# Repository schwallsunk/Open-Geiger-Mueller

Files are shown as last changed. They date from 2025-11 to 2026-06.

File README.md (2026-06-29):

# Open Geiger Müller Counter

This repository should provide all the needed parts for the construction of low-cost entry-level Geiger Müller (GM) counter system. This counter was build by request from the students of 151-0163-00L  Nuclear Energy Conversion at ETH Zürich. For a more complete description of the project please read the [manual](https://github.com/schwallsunk/Open-Geiger-Mueller/blob/main/Geiger_counter_manual_final.pdf).

The repository itself is subdivided into two two main parts. The hardware parts contains all the relevant EDA files created in KiCAD v9. The software directory contains all the different code written and tested for and on the hardware.

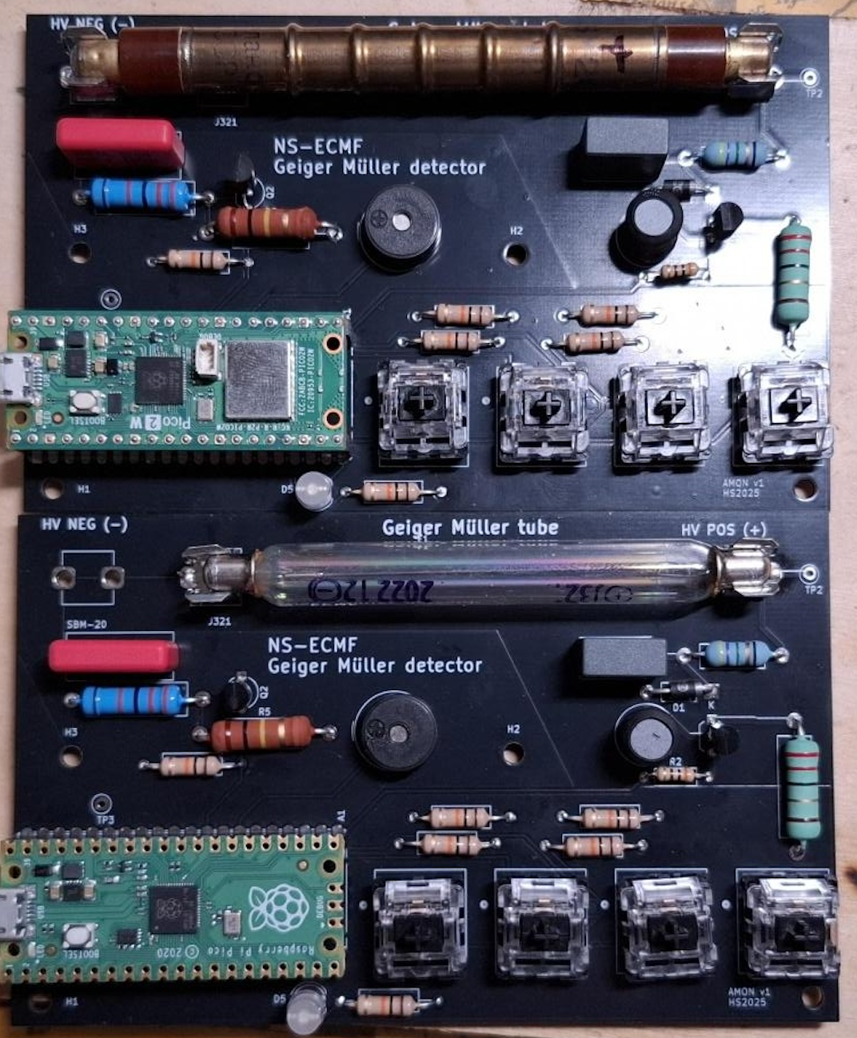
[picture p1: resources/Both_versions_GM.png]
Both GM-counters completed with J321 GM-tube as well as SBM-20 tube


## The Geiger Müller chamber :radioactive:
The detector is based on either the chinese J321 GM-tube or the soviet SBM-20 GM-tube (can be varied by soldering the negative receptacle either into the spot closer or further away from the HV terminal). The J321 can be easily bought through Aliexpress or ebay whereas for the SBM-20 tube you need to revert to ebay only. 
Due to the overall bigger detection volume of the SBM-20 tube compared with the J321 tube, the sensitivity of the soviet tube will be much higher at the cost of roughly double the price of the J321 tube.

## Microcontroller
The microcontroller of choice here is the Rasperry Pico 2W (rp2350 + wifi chipset), allowing for programming in a multitude of languages (Micropython, Arduino, C++, C), lowering the overall barrier to entry into microcontroller (uC) programming. But the PCB itself also supports the Pico W or any other uC with a fitting pin out. 
The W version of the uC also offers a wireless chip set which supports WiFi as well as Bluetooth connectivity, for which a micropython example is available. This example sends the activity according to the Bluetooth LE standard wirelessly to a receiving device. 
But in case of budgetary concerns, a Rasperry Pico can also be used as a drop-in replacement. The RISC-V-based implementation in this repository might then not work, though.

### Without IDE install
For an easier starting point, there is a precompiled firmware already available in this repository under [FW-file](https://github.com/schwallsunk/Open-Geiger-Mueller/blob/main/software/cpp/Counter_cpp_RISC-V.uf2). This file can be easily flashed by holding down the only button on the Raspberry Pico and plugging it into the USB port of the PC. 
The Pico will then appear as a mass storage device (The button on the Pico can be released at this point ) onto which the given firmware .uf2 file can be dragged and dropped onto it. The microcontroller will reboot by itself as soon as the new firmware file is fully transferred.
From there on, the clicking noise of the background radiation should be heard.

### IDE firmware development
If the goal is to do micropython code development, the following documentation [chapter 4](https://datasheets.raspberrypi.com/pico/raspberry-pi-pico-python-sdk.pdf) might be useful. All the given Micropython examples can be copied and pasted into the IDE and directly deployed. 
For the C/C++ code part, there is either a way to do full code development with the [C/C++ IDE](https://pip-assets.raspberrypi.com/categories/610-raspberry-pi-pico/documents/RP-008276-DS-1-getting-started-with-pico.pdf?disposition=inline), where the given code example can be copied and pasted into the given editor and then, at a later stag,e converted into a binary.  

## Electronics

### Parts sourcing
The sourcing of the components for this project was done entirely through the [LCSC](https://www.lcsc.com/) except for the GM-tube as well as the Raspberry Pico 2W. The GM-tube was bought off [EBAY SBM-20 search](https://www.ebay.com/sch/i.html?_nkw=sbm20&_sacat=0&_from=R40&_trksid=p4624852.m570.l1313) and the Pico 2W can be bought from your local electronics reseller.

### PCB manufacturing
The custom printed circuit board (PCB) itself was produced by sending the relevant gerber files to [JLCPCB](https://www.jlcpcb.com/) and choosing a black finish apart from that there is nothing special to consider when ordering them. The relevant gerber files are all merged into a single zip. This zip can be found in the hardware part of this repository.

### BOM 
| LCSC part number | Part description                                          | Amount | Price per piece (USD/piece) | Label of Part on PCB                    |
|------------------|-----------------------------------------------------------|--------|-----------------------------|----------------------------------------|
| C252915          | 2.048kHz 3.3V Electromagnetic Through Hole Buzzer         | 1      | 0.1854                      | BZ1                                    |
| C49234238        | Through Hole Pushbutton Switches RoHS                     | 4      | 0.0809                      | SW1, SW2, SW3, SW4                     |
| C2894588         | Carbon Film Resistor 300Ω                                 | 1      | 0.0043                      | R2                                     |
| C122827          | Metal Film Resistor 22Ω 3W                                | 1      | 0.0392                      | R1                                     |
| C2686215         | 10nF -40°C~+110°C ±5% 1kV)                                | 1      | 0.0969                      | C1                                     |
| C714352          | Carbon Film Resistor 10kΩ 500mW                           | 6      | 0.0081                      | R6,R8,R10,R11,R12,R13                  |
| C142864          | Cylindrical Clip Through Hole,P=7.6mm Fuseholders RoHS    | 2      | 0.1619                      | HV POS (+) and either J321 or SBM-20   |
| C20613339        | 20mA 5 mm flat-head LED                                   | 1      | 0.1041                      | D5                                     |
| C433559          | Metal Film Resistor 22kΩ 3W                               | 1      | 0.0549                      | R4                                     |
| C5156722         | 40V 625mW 200mA NPN TO-92 Single Bipolar Transistors RoHS | 1      | 0.0391                      | Q2                                     |
| C30190409        | Glass Glaze Resistor 4.7MΩ                                | 1      | 0.0553                      | R3                                     |
| C2924242         | 100mA 10mH ±10% Drum-core inductor                        | 1      | 0.173                       | L1                                     |
| C152300          | 30A 175ns 600V 1V@1A 1A DO-41 Single Diodes RoHS          | 1      | 0.0655                      | D1 => look at polarity when installing |
| C256388          | 400V 2.1W 1.5A NPN TO-92 Single Bipolar Transistors RoHS  | 1      | 0.1451                      | Q1                                     |
| C122214          | 100kΩ 1W ±250ppm/°C                                       | 1      | 0.0923                      | R5                                     |
| C7499336         | Pin header 2.54mm 20P                                     | 2      | 0.1601                      | A1 both rows                           |
| C434407          | 220pF capacitor                                           | 1      | 0.2914                      | C2                                     |

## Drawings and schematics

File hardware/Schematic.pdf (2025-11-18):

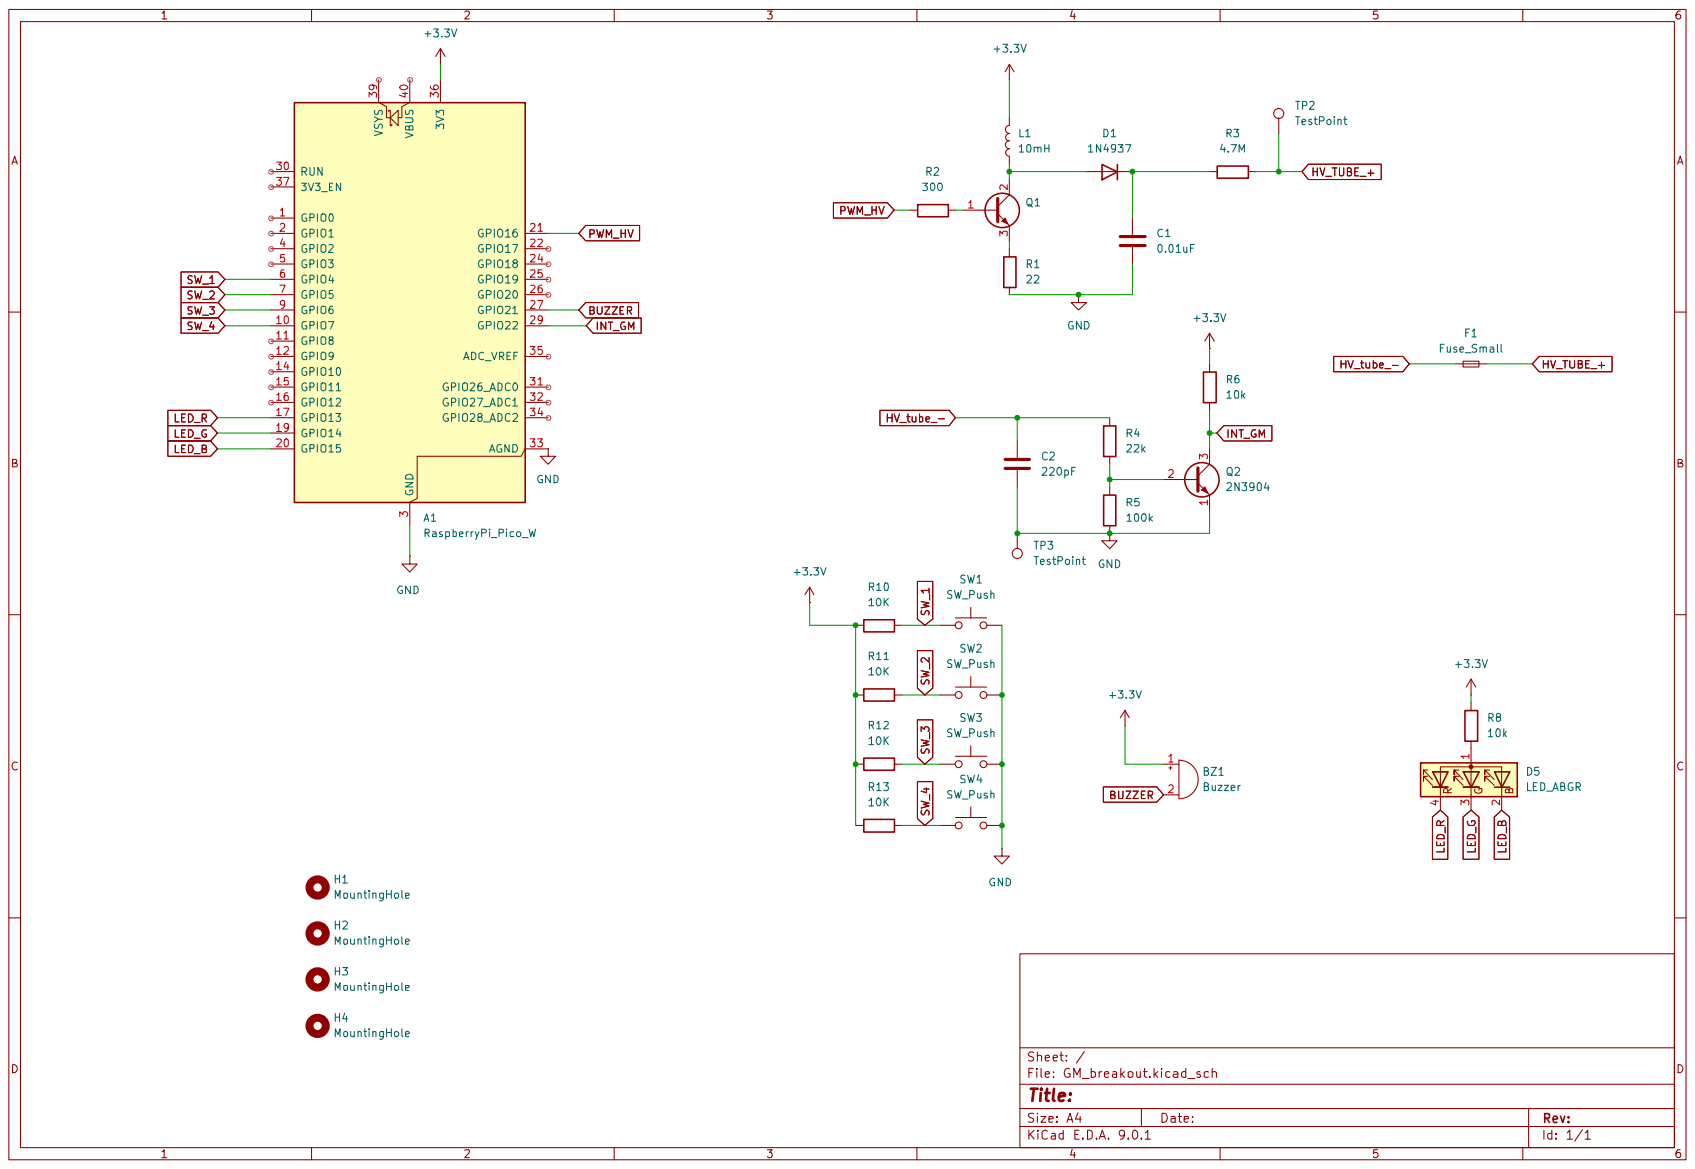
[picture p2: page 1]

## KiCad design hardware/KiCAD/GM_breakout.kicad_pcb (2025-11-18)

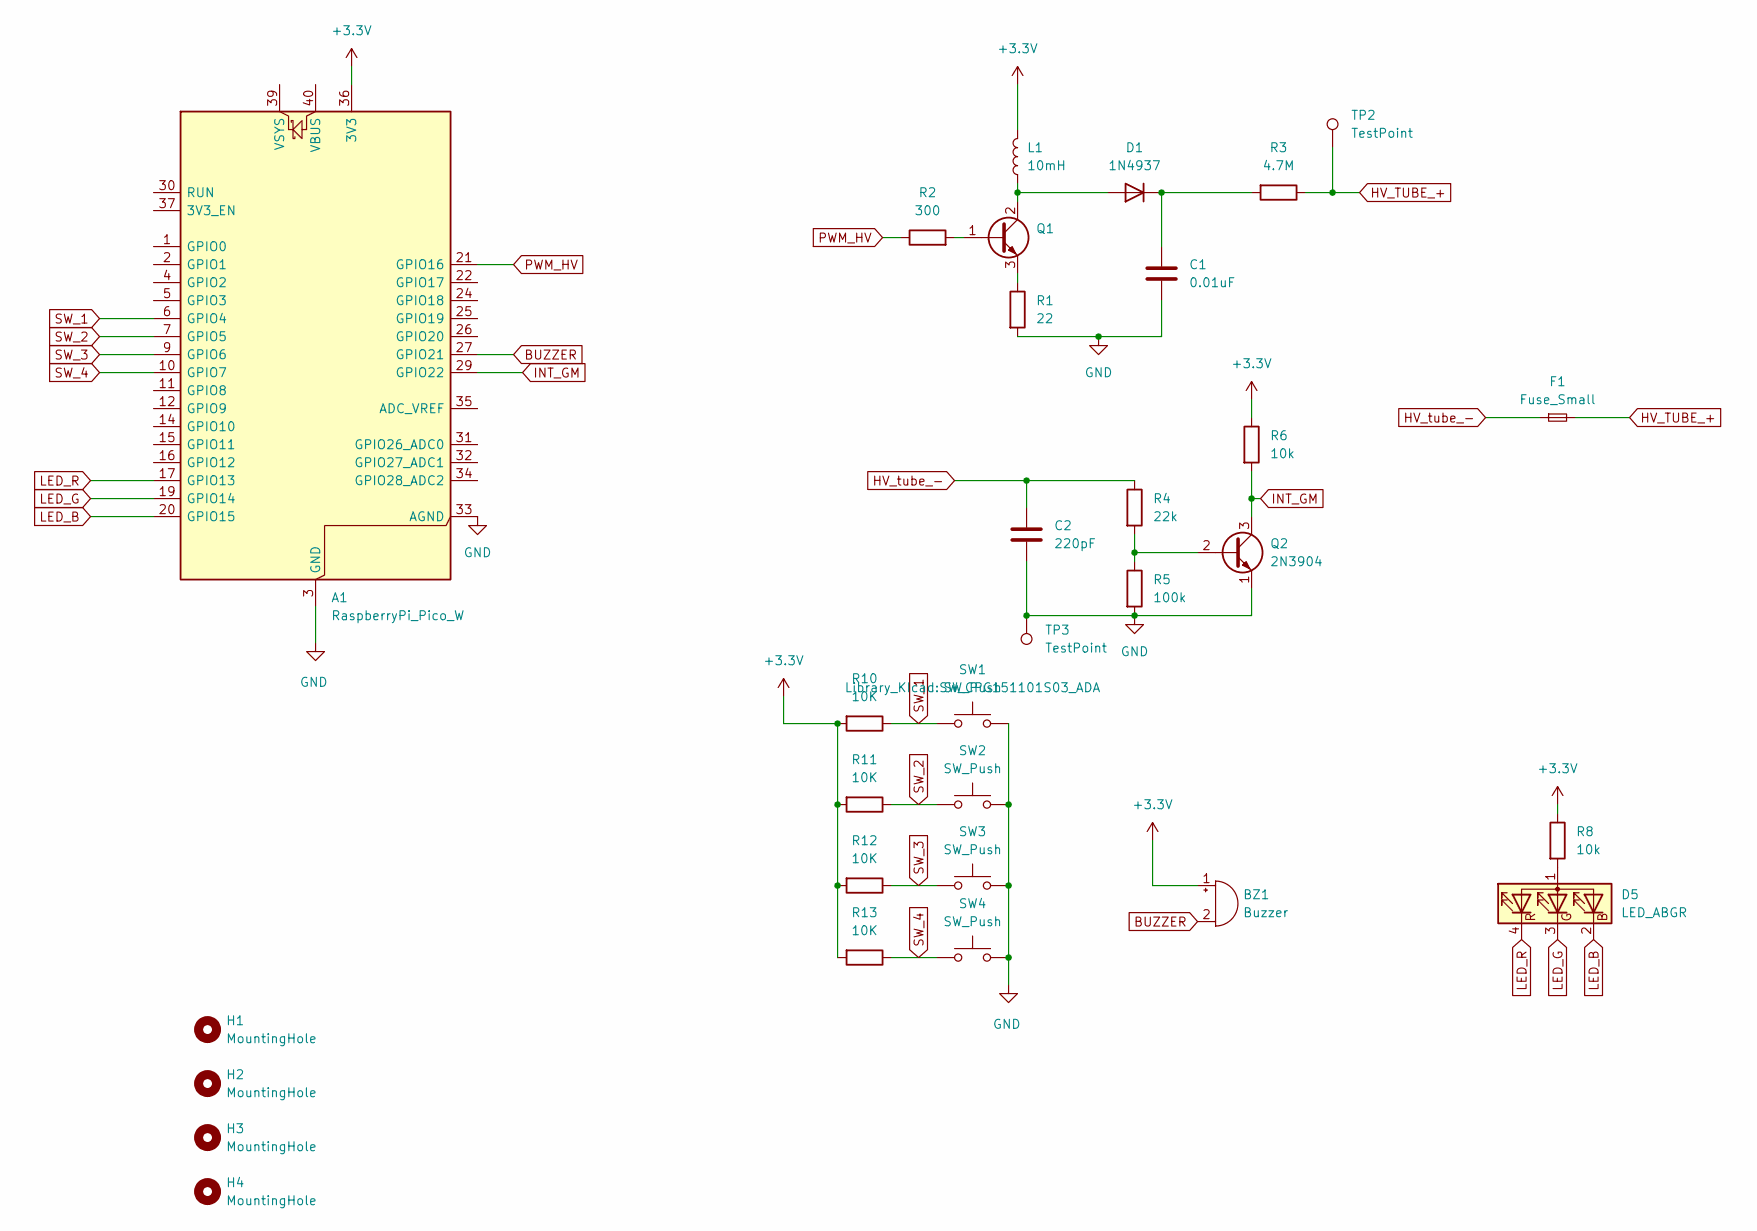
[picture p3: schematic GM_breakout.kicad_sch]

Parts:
A1: RaspberryPi_Pico_W; RaspberryPi_Pico_Common_Unspecified
BZ1: Buzzer; Buzzer_TDK_PS1240P02BT_D12.2mm_H6.5mm
C1: 0.01uF; C_Rect_L11.0mm_W6.3mm_P10.00mm_MKT
C2: 220pF; C_Rect_L16.5mm_W7.3mm_P15.00mm_MKT
D1: 1N4937; D_DO-41_SOD81_P10.16mm_Horizontal
D5: LED_ABGR; LED_D5.0mm-4_RGB
F1: Fuse_Small; SBM-20_GM_holder
H1, H2, H3, H4: MountingHole; MountingHole_3.2mm_M3_ISO14580
L1: 10mH; L_Radial_D9.5mm_P5.00mm_Fastron_07HVP
Q1: MJE13003; TO-92_Inline_Wide
Q2: 2N3904; TO-92_Inline_Wide
R1: 22; R_Axial_DIN0516_L15.5mm_D5.0mm_P20.32mm_Horizontal
R2: 300; R_Axial_DIN0207_L6.3mm_D2.5mm_P10.16mm_Horizontal
R3: 4.7M; R_Axial_DIN0411_L9.9mm_D3.6mm_P15.24mm_Horizontal
R4: 22k; R_Axial_DIN0516_L15.5mm_D5.0mm_P20.32mm_Horizontal
R5: 100k; R_Axial_DIN0414_L11.9mm_D4.5mm_P20.32mm_Horizontal
R6, R8: 10k; R_Axial_DIN0309_L9.0mm_D3.2mm_P15.24mm_Horizontal
R10, R11, R12, R13: 10K; R_Axial_DIN0309_L9.0mm_D3.2mm_P15.24mm_Horizontal
SW1, SW2, SW3, SW4: SW_Push; SW_CPG151101S03_ADA
TP2, TP3: TestPoint; TestPoint_Loop_D2.50mm_Drill1.0mm

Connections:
+3.3V: A1.36 (3V3), BZ1.1 (+), L1.2, R6.1, R8.1, R10.2, R11.2, R12.2, R13.2
BUZZER: A1.27 (GPIO21), BZ1.2 (-)
GND: A1.3 (GND), A1.8 (GND), A1.13 (GND), A1.18 (GND), A1.23 (GND), A1.28 (GND), A1.33 (AGND), A1.38 (GND), C1.2, C2.2, Q2.1 (E), R1.2, R5.2, SW1.2, SW2.2, SW3.2, SW4.2, TP3.1
HV_TUBE_+: F1.2, R3.1, TP2.1
HV_tube_-: C2.1, F1.1, R4.1
INT_GM: A1.29 (GPIO22), Q2.3 (C), R6.2
LED_B: A1.20 (GPIO15), D5.2 (BK)
LED_G: A1.19 (GPIO14), D5.3 (GK)
LED_R: A1.17 (GPIO13), D5.4 (RK)
unnamed: D1.2 (A), L1.1, Q1.2 (C)
unnamed: C1.1, D1.1 (K), R3.2
unnamed: D5.1 (A), R8.2
unnamed: Q1.1 (B), R2.2
unnamed: Q1.3 (E), R1.1
unnamed: Q2.2 (B), R4.2, R5.1
PWM_HV: A1.21 (GPIO16), R2.1
SW_1: A1.6 (GPIO4), R10.1, SW1.1
SW_2: A1.7 (GPIO5), R11.1, SW2.1
SW_3: A1.9 (GPIO6), R12.1, SW3.1
SW_4: A1.10 (GPIO7), R13.1, SW4.1

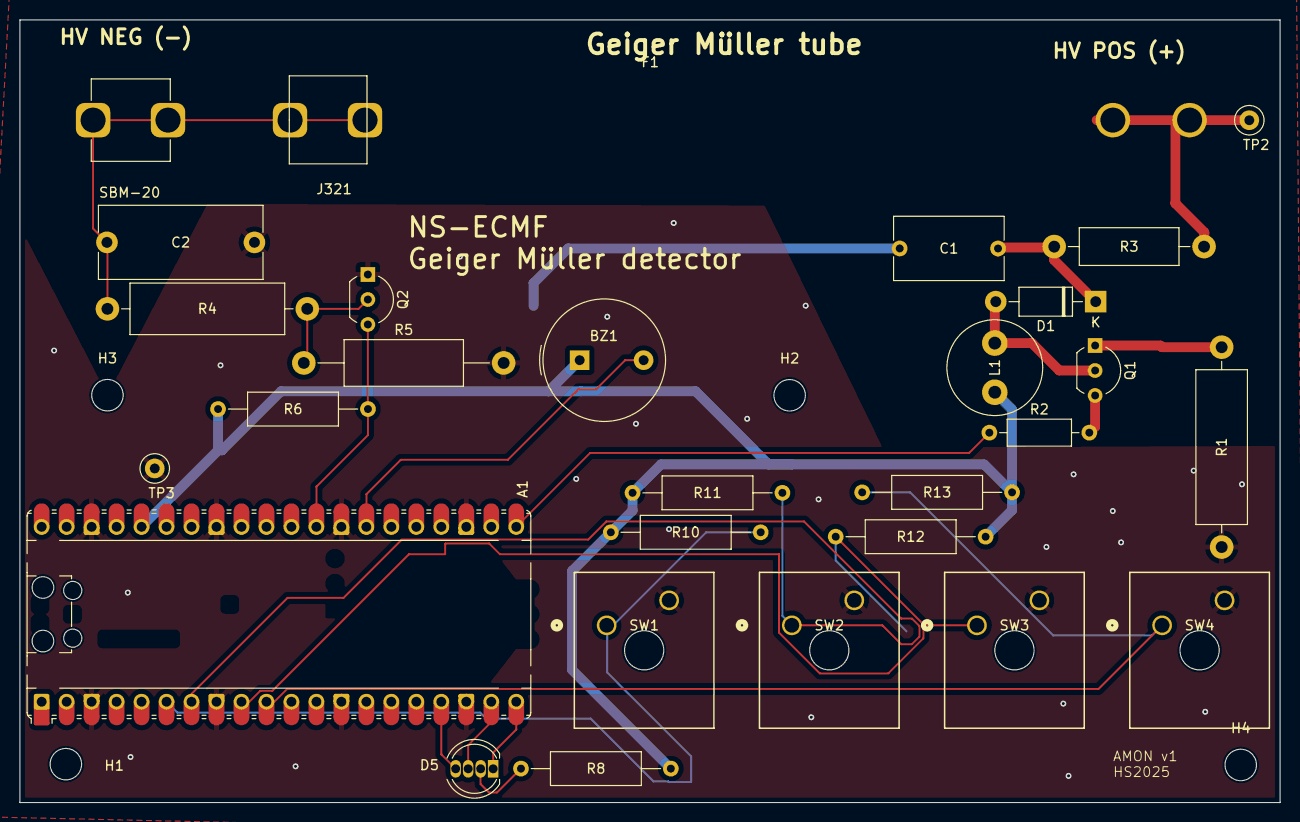
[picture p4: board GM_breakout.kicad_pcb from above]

Board: 2 copper layers, 128.1 x 79.6 mm, 31 parts (0 on the bottom side), 20 nets.

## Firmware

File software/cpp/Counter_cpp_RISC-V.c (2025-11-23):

// __author__ = "Saioul Ngoun and Axel Monney"
// __copyright__ = "Copyright 2025, Open Geiger Mueller project"
// __license__ = "GPL"
// __version__ = "1.0.0"
// __status__ = "Production"




#include <stdio.h>
#include "pico/stdlib.h"
#include "hardware/timer.h"
#include "hardware/gpio.h"
#include "hardware/pwm.h"

const uint16_t PERIOD_INTEGRATION_COUNTS = 1000U;  // Interrupt period in ms within which the counts are being averaged for
const uint8_t HV_TUBE_INT_PIN = 22U; // Geiger tube interrupt for ionization counting
const uint8_t HV_TUBE_PSU_PIN = 16U; // HV tube high voltage (HV) switching power supply stimulus pin
const uint8_t BUZZER_PIN = 21U; // Pin on which Piezo buzzer is hooked up to
const uint8_t LED_R_PIN = 13U; // Pin for the red color of the RGB LED
const uint8_t LED_G_PIN = 14U; // Pin for the green color of the RGB LED
const uint8_t LED_B_PIN = 15U; // Pin for the blue color of the RGB LED
const uint8_t SWITCH_1_PIN = 4U; // Pin for the switch 1 labelled SW1 on PCB
const uint8_t SWITCH_2_PIN = 5U; // Pin for the switch 2 labelled SW2 on PCB 
const uint8_t SWITCH_3_PIN = 6U; // Pin for the switch 3 labelled SW3 on PCB
const uint8_t SWITCH_4_PIN = 7U; // Pin for the switch 4 labelled SW4 on PCB 

uint16_t counts_array_moving_avg[10]; // Moving window array for averaged cps value
volatile uint16_t counter = 0;
volatile bool Buzzer_state = 0;
static repeating_timer_t timer; // struct used for the repeating measurement timer interrupt
volatile bool Flag_thread_lock = false;
volatile uint8_t counter_location = 0;

void counter_callback(){
    irq_set_enabled(IO_IRQ_BANK0,false);
    counter++;
    Buzzer_state = !Buzzer_state;
    gpio_put(BUZZER_PIN,Buzzer_state);
    irq_set_enabled(IO_IRQ_BANK0,true);
}

void print_measurements(uint16_t *buf,
                const uint size_buf){
  for(uint i=0; i<size_buf;i++){
    printf("%u,",*(buf+i));
    }
  printf("\n");
}

void print_bequerel(uint16_t *buf,
                const uint size_buf){
    uint32_t total_count = 0;
    double total_activity = 0.;
    for(uint i=0; i<size_buf;i++){
    total_count=*(buf+i)+total_count;
    }
    total_activity = total_count/(size_buf*(PERIOD_INTEGRATION_COUNTS/1000));
    printf("The total acitvity in of the sample is %e Bq",total_activity);
    printf("\n");
    printf("The total amount of decays in of the sample over the last 10 seconds are %u decays",total_count);
    printf("\n");
    }

bool alarm_callback(repeating_timer_t *t) {
    if (counter_location < 10){
        counter_location++;
        counts_array_moving_avg[counter_location] = counter;
    }
    else{
        counts_array_moving_avg[0] = counter;
        counter_location = 0;
    }
    counter = 0;
    return true;
}

int main()
{
    stdio_init_all();

    // Setup of all GPIOs
    gpio_set_irq_callback(&counter_callback);
    gpio_set_irq_enabled(HV_TUBE_INT_PIN, GPIO_IRQ_EDGE_FALL, true);
    gpio_init(BUZZER_PIN); gpio_set_dir(BUZZER_PIN, GPIO_OUT);gpio_put(BUZZER_PIN,1);
    gpio_set_function(HV_TUBE_PSU_PIN, GPIO_FUNC_PWM);
    uint slice_num = pwm_gpio_to_slice_num(HV_TUBE_PSU_PIN); // find out to which slice Pin16 is connected to => should be slice 0
    pwm_set_wrap(slice_num, 25000); // Setting period lenght in clock cycles here for cpu clocked at 150MHz
    pwm_set_chan_level(slice_num, 0, 21500); // When to break circuit 
    pwm_set_enabled(slice_num, true);
    printf("HV is on!\n");
    gpio_init(LED_R_PIN); gpio_set_dir(LED_R_PIN, GPIO_OUT);gpio_put(LED_R_PIN,0);
    gpio_init(LED_G_PIN); gpio_set_dir(LED_G_PIN, GPIO_OUT);gpio_put(LED_G_PIN,0);
    gpio_init(LED_B_PIN); gpio_set_dir(LED_B_PIN, GPIO_OUT);gpio_put(LED_B_PIN,1);
    gpio_init(SWITCH_1_PIN); gpio_set_dir(SWITCH_1_PIN, GPIO_IN);gpio_pull_up(SWITCH_1_PIN);
    gpio_init(SWITCH_2_PIN); gpio_set_dir(SWITCH_2_PIN, GPIO_IN);gpio_pull_up(SWITCH_2_PIN);
    gpio_init(SWITCH_3_PIN); gpio_set_dir(SWITCH_3_PIN, GPIO_IN);gpio_pull_up(SWITCH_3_PIN);
    gpio_init(SWITCH_4_PIN); gpio_set_dir(SWITCH_4_PIN, GPIO_IN);gpio_pull_up(SWITCH_4_PIN);
    gpio_init(HV_TUBE_INT_PIN); gpio_set_dir(HV_TUBE_INT_PIN, GPIO_IN);gpio_pull_up(SWITCH_4_PIN);
    irq_set_enabled(IO_IRQ_BANK0,true);
    add_repeating_timer_ms(PERIOD_INTEGRATION_COUNTS, alarm_callback, NULL, &timer);

    while (true) {
        if(!gpio_get(SWITCH_1_PIN)){
        print_measurements(counts_array_moving_avg,10);
        sleep_ms(1000);
        }
        if(!gpio_get(SWITCH_2_PIN)){
        print_bequerel(counts_array_moving_avg,10);
        sleep_ms(1000);
        }
        tight_loop_contents();
    }
    cancel_repeating_timer (&timer);
}

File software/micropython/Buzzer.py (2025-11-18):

__author__ = "Saioul Ngoun and Axel Monney"
__copyright__ = "Copyright 2025, NS-ECMF Open Geiger Mueller project"
__license__ = "GPL"
__version__ = "1.0.0"
__status__ = "Production"


from machine import Pin,PWM
from utime import sleep


total = 0 


pin = Pin("LED", Pin.OUT)
pin_B = Pin(14,Pin.OUT)
pin_G = Pin(15,Pin.OUT)
pin_R = Pin(13,Pin.OUT)

switch_1 = Pin(4, Pin.IN, Pin.PULL_UP)
switch_2 = Pin(5, Pin.IN, Pin.PULL_UP)
switch_3 = Pin(6, Pin.IN, Pin.PULL_UP)
switch_4 = Pin(7, Pin.IN, Pin.PULL_UP)

buzzer = Pin(21,Pin.OUT)

hv_tube_plus = Pin(16, Pin.OUT)
hv_tube_neg = Pin(22, Pin.IN)

pwm_hv_plus=PWM(hv_tube_plus)


pin_B.high()
pin_G.high()
pin_R.high()

pwm_hv_plus.freq(6000)
print("HV gets turned on")
pwm_hv_plus.duty_u16(55000)

while True:
    try:
        if not switch_1.value():
            print("button is pressed")
            pin_B.toggle()
            sleep(0.2) # sleep 1sec
            pin_G.toggle()
            sleep(0.2)
            pin_R.toggle()
            print("Done with my light spiel")
        if not switch_2.value():
            print("Button 2")
            print(total)
            #pwm_buzz.duty_u16(30000)
        if not switch_3.value():
            #pwm_buzz.duty_u16(0)
            print("button 3")
        if not switch_4.value():
            pwm_hv_plus.duty_u16(0)
            print("HV is off") 
        if not hv_tube_neg.value():
            buzzer.toggle()
            pin_R.toggle()
    except KeyboardInterrupt:
        break
print("Finished.")

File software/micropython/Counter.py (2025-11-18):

__author__ = "Saioul Ngoun and Axel Monney"
__copyright__ = "Copyright 2025, NS-ECMF Open Geiger Mueller project"
__license__ = "GPL"
__version__ = "1.0.0"
__status__ = "Production"



from machine import Pin,PWM,Timer
from utime import sleep
import micropython

micropython.alloc_emergency_exception_buf(100)
PERIOD_OF_COUNTER = 500

# Setup of counter values and arrays

total = 0 

floating_avg_arr = [0,0,0,0,0,0,0,0,0,0]

# General setup of I/O pins in which direction which pins operate

pin = Pin("LED", Pin.OUT)
pin_R = Pin(13,Pin.OUT)
pin_G = Pin(15,Pin.OUT)
pin_B = Pin(14,Pin.OUT)

# Ensure initial state of RGB LED pins
pin_B.high() 
pin_G.high()
pin_R.high()




switch_1 = Pin(4, Pin.IN, Pin.PULL_UP)
switch_2 = Pin(5, Pin.IN, Pin.PULL_UP)
switch_3 = Pin(6, Pin.IN, Pin.PULL_UP)
switch_4 = Pin(7, Pin.IN, Pin.PULL_UP)

buzzer = Pin(21,Pin.OUT)

hv_tube_plus = Pin(16, Pin.OUT) # PWM of switching HV transformer transistor
hv_tube_neg = Pin(22, Pin.IN) # Output that falls low if ionization is detected


# Setup of HV switching PSU timing
pwm_hv_plus=PWM(hv_tube_plus)   # Setup of PWM pin for the HV transformer to ensure the HV supply of the tube
pwm_hv_plus.freq(6000) # frequency of PWM signal
print("HV gets turned on")
pwm_hv_plus.duty_u16(55705) # Duty cycle of PWM signal


# Interrupt function for counting ionizations in tube
def handle_interrupt(Pin):
    global total
    total = total+1
    buzzer.toggle()

def handle_counter(Pin):
    global total
    global floating_avg_arr
    floating_avg_arr.pop(0)
    floating_avg_arr.append(total)
    total = 0

tim = Timer(-1,period=PERIOD_OF_COUNTER, mode=Timer.PERIODIC, callback=handle_counter)
tim.init(period=PERIOD_OF_COUNTER, mode=Timer.PERIODIC, callback=handle_counter)
# Interrupt handle setup for ionization
irq_ionization = hv_tube_neg.irq(trigger=Pin.IRQ_FALLING, handler=handle_interrupt)



def count():
    global floating_avg_arr
    total_counts = sum(floating_avg_arr)
    counts_per_second = total_counts/(len(floating_avg_arr)*PERIOD_OF_COUNTER/1000)
    return counts_per_second

    #pwm.deinit()

while True:
    try:
        if not switch_1.value():
            print("button is pressed")
            pin_B.toggle()
            sleep(0.2) # sleep 1sec
            pin_G.toggle()
            sleep(0.2)
            pin_R.toggle()
            print("Done with my light spiel")
        if not switch_2.value():
            print("Button 2")
            cps=count()
            print(total)
            print("Total CPS is:")
            print(cps)
            #pwm_buzz.duty_u16(30000)
        if not switch_3.value():
            #pwm_buzz.duty_u16(0)
            print("button 3")
        if not switch_4.value():
            pwm_hv_plus.duty_u16(0)
            print("HV is off") 
    except KeyboardInterrupt:
        break
print("Finished.")
